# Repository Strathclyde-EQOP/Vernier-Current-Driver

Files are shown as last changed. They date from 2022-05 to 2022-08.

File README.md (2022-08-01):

# Vernier Current Driver

The Vernier Current Driver is an ultra low noise, programmable, bi-polar current source. It comes in two flavours:

1. Low Current Driver (LCD): designed to output current up to ~50 mA
2. High Current Driver (HCD): designed to output currents from ~50 mA to ~250 mA

## Releases

Checkout the [latest release](https://github.com/Strathclyde-EQOP/Vernier-Current-Driver/releases/latest) to download the latest verified version of the design. Releases include PDF schematics and gerber files, so there is no need to install/understand KiCAD in order to make a board.

Checkout the [dev branch](https://github.com/Strathclyde-EQOP/Vernier-Current-Driver/tree/dev) for the most up to date (but probably untested!) design.

## Performance

Three sample devices have been tested. For full details, see the companion paper or take a look a look in the [Testing](/Doc/Testing/) folder.

The headlines results:

|Configuration|CH1|CH2|CH3|
|---|---|---|---|
|LCD@10 mA<sub>MAX</sub> (10 ± 5 Hz average noise) | 151.1 pA√Hz | 147.4 pA√Hz | 146.3 pA√Hz |
|LCD@2.5 mA<sub>MAX</sub> (10 ± 5 Hz average noise) | 37.6 pA√Hz | 38.2 pA√Hz | 37.7 pA√Hz |
|HCD@250 mA<sub>MAX</sub> (10 ± 5 Hz average noise) | 4114.2 pA√Hz | 4125.3 pA√Hz | 4124.1 pA√Hz |
|LCD@10 mA<sub>MAX</sub> (10 ± 5 Hz relative average noise) | 15.05 ppb√Hz | 14.68 ppb√Hz | 14.57 ppb√Hz |
|LCD@2.5 mA<sub>MAX</sub> (10 ± 5 Hz relative average noise) | 15.06 ppb√Hz | 15.29 ppb√Hz | 15.10 ppb√Hz |
|HCD@250 mA<sub>MAX</sub> (10 ± 5 Hz relative average noise) | 16.46 ppb√Hz | 16.50 ppb√Hz | 16.50 ppb√Hz |

noise_spectra

## Manual

For more information checkout the [Getting Started Guide](Doc/README.md).

## Publication

If you're the academic type, lots more detail on the design and testing of the Vernier Current Source can be found in our open-access paper, available as a pre-print on [arXiv](https://arxiv.org/abs/2207.10348).

## Citing

When citing this work in an academic context, please cite the paper as you normally would.

Outside of academic work, please link directly to this GitHub repo.

Lastly, if you make one and you like it (or don't like it), we would love to know!

## License

This work is licensed under a [Creative Commons Attribution-ShareAlike 4.0 International License](https://creativecommons.org/licenses/by-sa/4.0/).

## Authors

This work was created by [Marcin Mrozowski](https://eqop.phys.strath.ac.uk/people/marcin-mrozowski/) and [Iain Chalmers](https://www.linkedin.com/in/iain-chalmers-0394753b)
from the [Experimental Quantum Optics and Photonics](http://photonics.phys.strath.ac.uk/)
group at the University of Strathclyde.

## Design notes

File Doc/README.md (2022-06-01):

# Getting Started

1. Decide which device you want to make. If the maximum current you need is <50 mA, use a Low Current Driver (LCD). For larger current, up to 250 mA, use a High Current Driver.
2. Decided the maximum output current and bandwith you need, and calculate the components you should use. See [Customising Vernier Current Sources](Customisation.md) for help.
3. If you make an HCD, don't forget to [bias the driving stage](HCD-Biasing.md).
4. Make an enclosure and get connected. See [Getting Connected](GettingConnected.md) for details.
5. Program the Arduino using [the sample firmware](/Software/CurrentDriverFirmware/README.md), or write your own. Don't forget to set the board-specific parameters that are stored in the EEPROM.
6. Use it in your application!

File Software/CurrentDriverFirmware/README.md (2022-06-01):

# Current Driver Firmware

This example Vernier Current Driver firmware is designed to run on an [Arduino Nano Every](), although a regular Nano is compatible in a pinch (with slightly reduced functionality). It can be used as the basis for writing your own custom firmware to drive the currents needed for specific applications.

# Libraries

This firmware makes use of the [Arduino-CommandParser library](https://github.com/Uberi/Arduino-CommandParser). You need to install the library before you can compile the firmware.

# Connection

Connect to the USB Serial interface using the application of your choice.

# Commands

All command packets are started with a `<` and end in a `>` character. The default serial is 1M-8-N-1.

Commands which query start with a `?`.

Commands which perform an action start with a `!`.

Respones to a command all start with a `#` and end with `\r\n`.

## Example

To set channel 1 to midrange (i.e. no current output), you would send the command `<!chan 1 32768>`.

### Command: `?`

**Description:**
Basic comms check.

**Arguments:**
None.

**Response:**
Always returns `#check`.

### Command: `?chan {channel_number}`

**Description:**
Get the current DAC code being output on {channel_number}. See the project wiki for details on how the DAC code and output current are related.

**Arguments:**
[0] - channel_number: Channel number to query, range 1 to 3.

**Response:**
Valid arguments result in a response in the form of `#{channel_number} {setpoint}`, confirming the set values.
Invalid arguments result in a reponse of `#ERROR`.

### Command: `!chan {channel_number} {setpoint}`

**Description:**
Set a channel to a specific DAC code. See the project wiki for details on how DAC code and output current are related.

**Arguments:**
[0] - channel_number: Channel number to update, range 1 to 3.
[1] - setpoint: DAC code to set channel to, range 0 to 65535.

**Response:**
Valid arguments result in a response in the form of `#{channel_number} {setpoint}`, confirming the set values.
Invalid arguments result in a reponse of `#ERROR`.

### Command: `!ramp {channel_number} {start} {step} {count}`

**Description:**
Setup a ramp output for a given channel. The start point is output immediately. Triggering the channel output (either with a !next command or via a trigger on a digital IO) will add {step} to the current output code. The output saturates after {count} triggers.

**Arguments:**
[0] - channel_number: Channel number to query, range 1 to 3.
[1] - start: The inital DAC count to output.
[2] - step: The number of DAC counts to increment by on a trigger.
[3] - count: The maximum number of triggers before the DAC output saturates.

**Response:**
Valid arguments result in a response in the form of `#{channel_number} {start} {step} {count}`, confirming the set values.
Invalid arguments result in a reponse of `#ERROR`.

### Command: `!next {channel_number}`

**Description:**
Triggers the given channel to move to the next output code.

**Arguments:**
[0] - channel_number: Channel number to query, range 1 to 3. Must be an integer.

**Response:**
Responds `#DONE` on success.
Responds `#ERROR {code}` on error. Error codes:

- -1: invalid channel.
- -2: channel not configured for stepping.

### Command: `?software`

**Description:**
Get the current software version string.

**Arguments:**
None.

**Response:**
The software version string in the form `#{version_string}`.

### Command: `?current`

**Description:**
Get the maximum output current in nanoamps.

**Arguments:**
None.

**Response:**
The maximum output current in the form `#{max_current} nA`.

### Command: `!current {max_current_nA}`

**Description:**
Set the maximum output current for the current driver in nanoamps.
The value is stored in EEPROM and persists between power cycles.

**Arguments:**
[0] - max_current_nA: The maximum output current in nA. Must be an integer.

**Response:**
Valid arguments result in a response in the form of `#{max_current_nA} nA`, confirming the set values.
Invalid arguments result in a reponse of `#ERROR`.

### Command: `?boardid`

**Description:**
Get the board ID.

**Arguments:**
None.

**Response:**
The board id string in the form `#{board_id}`.

### Command: `!boardid {id}`

**Description:**
Set the board ID.
The value is stored in EEPROM and persists between power cycles.

**Arguments:**
[0] - id: A string of up to 15 characters. Longer strings will be truncated.

**Response:**
The board id in the form `#{board_id}`.

### Command: `?hardware`

**Description:**
Get the hardware version.

**Arguments:**
None.

**Response:**
The hardware version string in the form `#{version_string}`.

### Command: `!hardware {version_string}`

**Description:**
Set the hardware version.
The value is stored in EEPROM and persists between power cycles.

**Arguments:**
[0] - version_string: A string of up to 15 characters. Longer strings will be truncated.

**Response:**
The hardware version in the form `#{version_string}`.

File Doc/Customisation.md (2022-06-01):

# Customising Vernier Current Drivers

To get the best noise performance, we recommend adapting the design to meet the requirements of specific applications. The two main specifications that can be adapted are the maximum output current and the output bandwidth.

# Setting The Maximum Output Current

The maximum output current for a Vernier Current Driver, $I_{max}$, should be configured to be as low as possible while still supplying the maximum current required. Doing so has two benefits:

1. The noise floor increases as $I_{max}$ increases (and is largely independent of what current the device is programmed to supply).
2. The current step size (i.e. the smallest programmable change in output current) increases with $I_{max}$.

## Configuring the LCD Maximum Output Current

The output of the LCD is based around a [Howland Current Pump](https://www.allaboutcircuits.com/technical-articles/the-howland-current-pump/) (HCP). Setting the output current on a channel requires changing 4 resistors. The excerpt below shows the HCP for Channel 1:

HCP

The current setting resistors are R38, R39, R44 and R45. The maximum output current is defined by the equation:

$$I_{max} = V_{REF} * \frac{1}{R_{f}}$$

where $R_{f} = R38 = R39 = R44 = R45$, and $V_{REF}$ is the reference voltage (2.5 V) from the LTC6655-2.5. As given in the schematic, $I_{max}=2.5\:mA$.

It is important that the resistor are of equal value, low tolerance (<= 0.1%) and low temperature coefficient (<= 25 ppm/°C). Changing the resistors will also require a change of the feedback capacitor (in this case C1) to maintain the previous bandwidth.

We have tested LCD devices configured for $I_{max}$ as low as 2.5 mA, and as high as 10 mA, but expect anything in the range of 25 μA to 50 mA to work.

## Configuring The HCD Maximum Output Current

Unlike the LCD, setting the maximum output current on the an HCD only requires changing one resistor per channel. The excerpt below shows the driving stage for Channel 1 on the HCD:

HCD

The current setting resistor is R48. The maximum output current is determined by the same equation as for the LCD:

$$I_{max} = V_{REF} * \frac{1}{R_{f}}$$

where $R_{f} = R48$, and $V_{REF}$ is the reference voltage (2.5 V) from the LTC6655-2.5. As given in the schematic, $I_{max}=192\:mA$.

If you change the feedback resistor on a board, don't forget to [re-adjust the transistor bias potentiometers](HCD-Biasing.md).

We have tested HCD devices with $I_{max}$ as high as 250 mA. For currents lower than 50 mA, it is better to use an LCD.

# Setting The Bandwidth

The output bandwidth of a Vernier Current Driver should be scaled to the intended application. For example in an application where the static field is set once and never changed, it would be advantageous to use a small bandwidth to reduce wideband noise. In an application that sweeps a static field, a wider bandwidth would be required.

The output bandwidth for all Vernier Current Drivers depends on the bandwidth of the inverting summer stage and the Sallen-Key filter stage. LCD devices also depend on the Howland Current Pump stage.

It is a good idea to set all filtering stages to the same cutoff frequency.

## Configuring the Inverting Summer Bandwidth

The inverting summer stage bandwidth is controlled by changing one capacitor. The excerpt below shows the inverting summer stage for Channel 1:

inverting_summer

To set the bandwidth, change the capacitor C34 based on the equation:

$$f_{-3db}=\frac{1}{2 \pi RC}$$

where $R=R29$ and $C=C34$. Note that R29 should **NOT** be adjusted to configure the bandwidth, as it would affect the summing circuit. In the example above, $f_c=159\:Hz$.

## Configuring the Sallen-Key Low Pass Filter Bandwidth

The bandwidth of the Sallen-Key low pass filter depends on two capacitors and two resistors. he excerpt below shows the Sallen-Key filtering stage for Channel 1:

sallen-key

The cutoff frequency for for the above low pass Sallen-Key filter is defined as:

$$f_{-3db}=\frac{1}{2 \pi R_{32} C_{52} R_{35} C_{49}}$$

It is recommended to leave the resistor values and only adapt the capacitor values to define the bandwidth.

## Configuring the Howland Current Pump Bandwidth (LCD Only)

Additional filtering is available on LCD devices by changing the feedback capacitor for the Howland Current Pump. The equation for the cuttoff frequency is:

$$f_{-3db}=\frac{1}{2 \pi RC}$$

where $R=R44$ and $C=C1$ in the excerpt in the [Configuring the LCD Maximum Output Current](#configuring-the-LCD-Maximum-Output-current) section.

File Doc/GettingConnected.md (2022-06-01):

# Getting Connected

## Enclosure

The Vernier Current Driver is designed to fit in a [Hammond 1455N1601](Doc/Customisation.md) enclosure. You can find our front/back panel machining template [here]().

Artboard 1

## Power

The coil driver is simple to operate. It requires a split rail power supply capable of supply ±11-16V: going beyond this range will trip the over-voltage protection. The device features a reverse polarity protection on it's power inputs.

## External Interface

The back panel features:

* **+V, GND, -V** - power inputs (accepts standard 4mm banana jacks).
* **ON/OFF switch** - this switch is a "soft" power switch which still supplies the power for the PG LEDs as well as low power indicator circuitry even when it is in "OFF" position. The standby current in this mode is less than 1 mA.
* **PG +V, PG -V LEDs** - power good LEDs that indicate input power has been applied in the correct polarity.
* **Battery low +V, -V** - low battery indicators. These LEDs will light up if the voltage falls below 11 V. Useful if you use lead-acid batteries to power the device.
* **PG +7.5V, +5V, -7.5V** - regulator power good indicators. These LEDs will light up if the PG flag has been raised for the ±7.5 V and 5 V rails.
* **Micro USB input** - USB interface for programming and control.

The front panel features:

* **Three output BNCs** - current output for each channel.
  * **_Note:_** BNCs on LCDs are _**referenced to ground**_ while HCD BNCs float via a resistor to ground. _**Do not**_ plug HCD output channels to any instrumentation that has a single-ended connection to ground!
* **RJ45 output** - an alternative output for the three channels. Pin arrangement CH1 (+ -) (7 8), CH2 (+ -) (4 5), CH3 (+ -) (1 2), GND (3 6). Useful for sending currents over inexpensive Cat5 twisted pairs.

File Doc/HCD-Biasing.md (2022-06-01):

# Biasing The Drive Transistors on HCDs

To ensure the HCD works as intended and does not go into thermal runaway, it is important to bias the driving transistors correctly using the onboard potentiometers. This can be achieved by using the potentiometers pair on each channel.

To correctly bias the transistors:

1. Power the HCD from a lab power supply with an adjustable current limit. Set the limit to 130% of $I_{max}$.
2. Set both potentiometers (RV1 and RV2) to 7 kΩ. You can check their resistance by probing TP55 and TP56 as well as TP57 and TP58 (or the equivalent on other channels).
3. Program the driver to supply maximum positive output current.
4. Connect the output to a current meter.
5. Adjust RV1 until you find the point where the current starts to drop from the maximum, then back off by half a turn (i.e. so that you are half a turn into the saturation region).
6. Program the driver to supply maximum negative output current and repeat for RV2.

Ideally, the device should be tested to ensure that no thermal-runaway condition is reached by changing the output current in the following order:

1. Max +ve current for 120 seconds
2. Zero current for 120 seconds
3. Max -ve current for 120 seconds.
4. Zero current for 120 seconds.

You can tell the device has gone into thermal runaway if, after returning to zero, the power draw from the supply does not drop. If the device goes into thermal runaway, the potentiometers need to be re-adjusted.

HCD

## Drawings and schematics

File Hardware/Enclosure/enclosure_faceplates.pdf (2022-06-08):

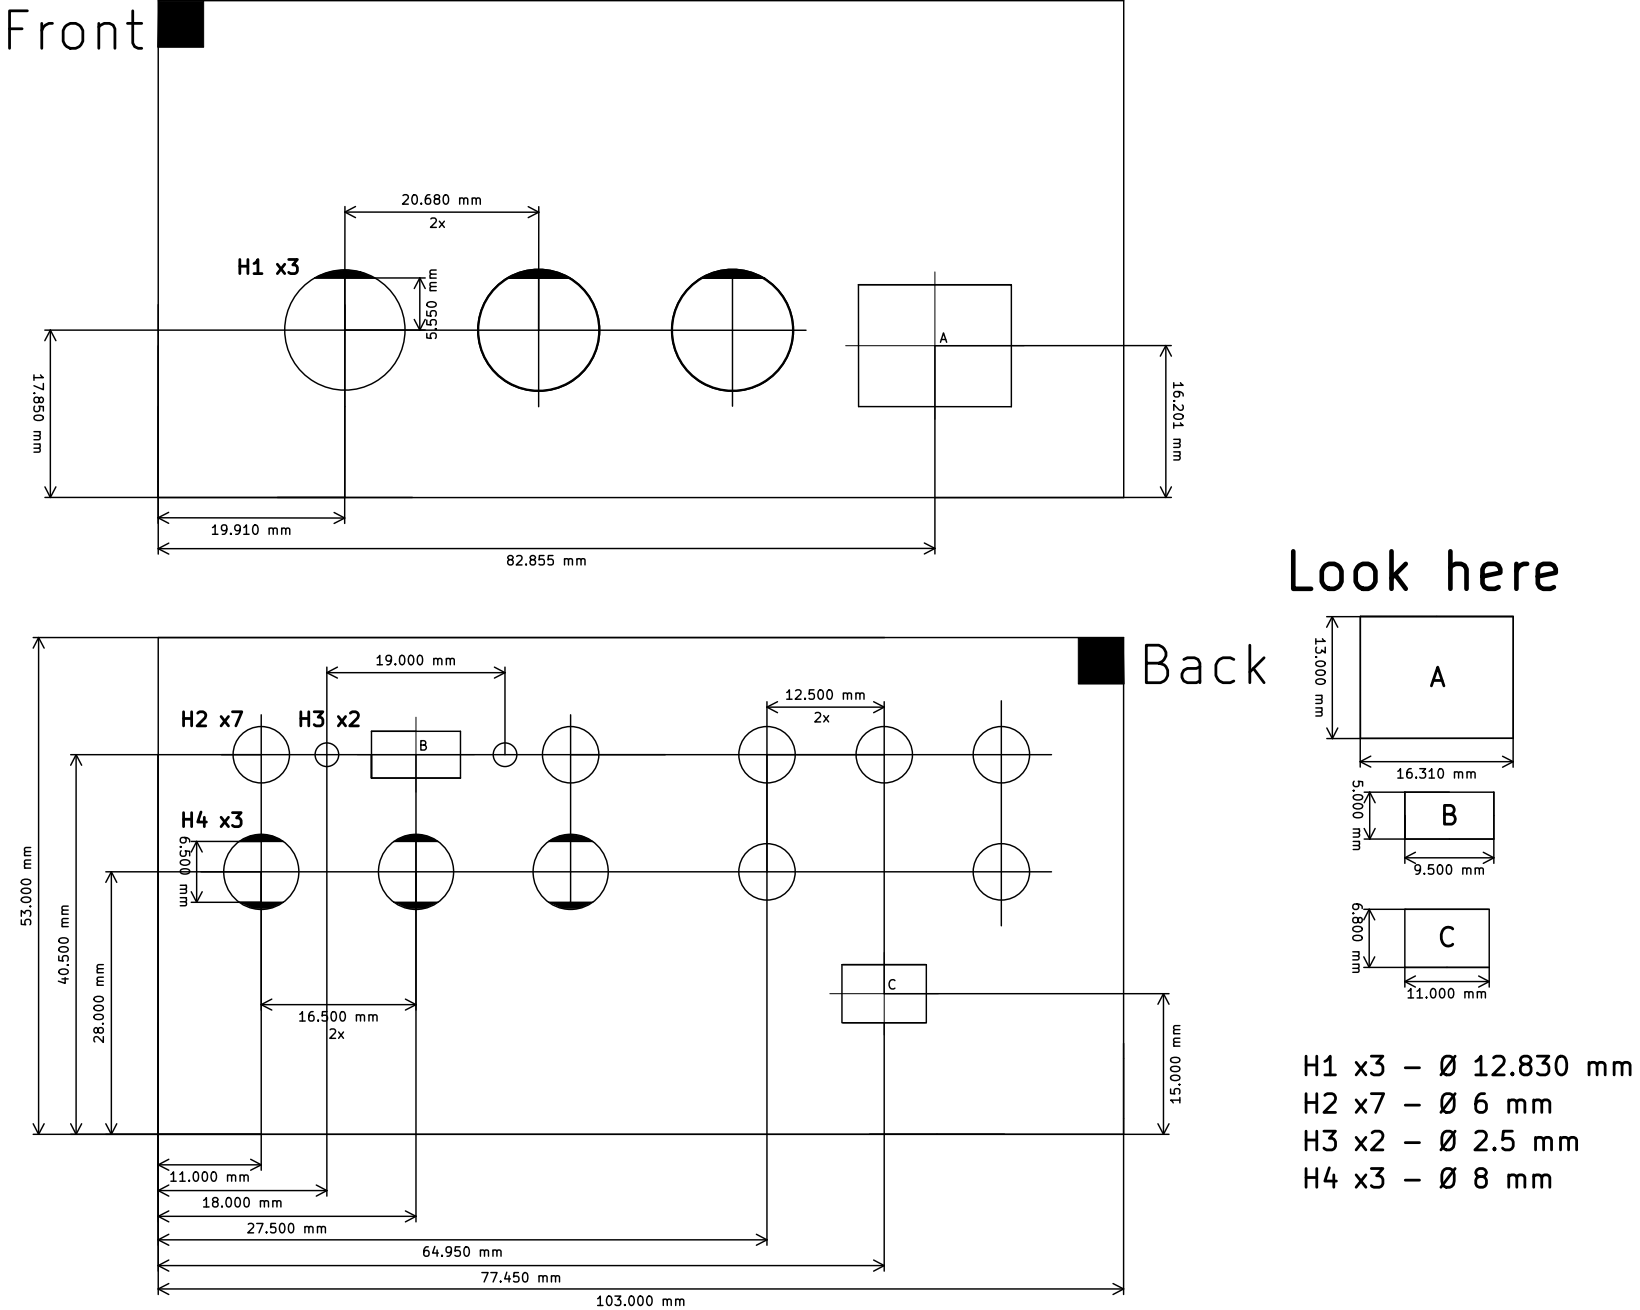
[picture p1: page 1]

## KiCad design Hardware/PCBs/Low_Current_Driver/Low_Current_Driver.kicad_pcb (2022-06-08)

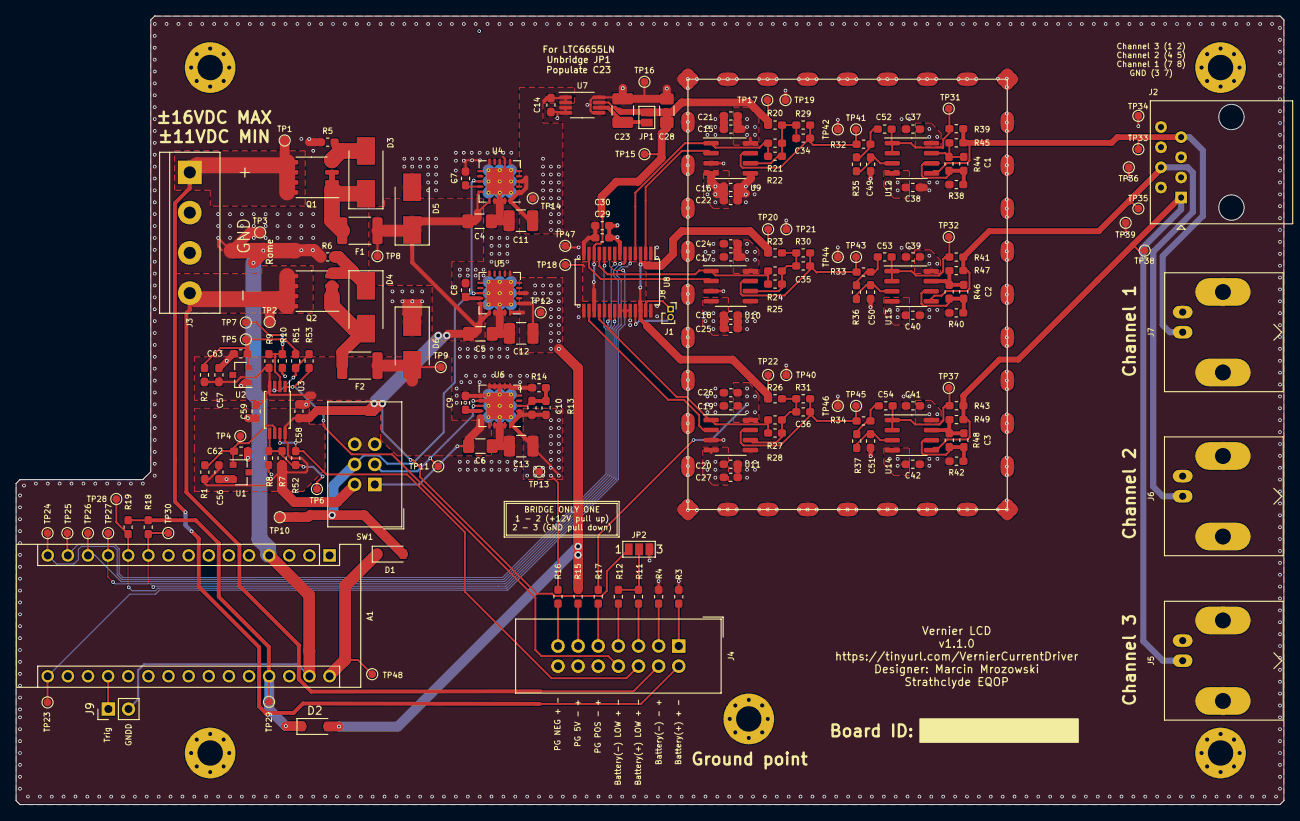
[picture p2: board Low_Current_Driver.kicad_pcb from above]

Board: 4 copper layers, 160.0 x 99.5 mm, 194 parts (0 on the bottom side), 78 nets.

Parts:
A1: Arduino_Nano_Every; Arduino_Nano
C1, C2, C3, C7, C8, C9, C21, C22, C24, C25, C26, C27, C49, C50, C51, C52, C53, C54: 1u; C_0603_1608Metric_Pad1.05x0.95mm_HandSolder
C4, C5, C6, C28: 10u; C_1206_3216Metric_Pad1.42x1.75mm_HandSolder
C10, C29: 10n; C_0603_1608Metric_Pad1.05x0.95mm_HandSolder
C11, C12, C13, C23: 47u; C_1210_3225Metric_Pad1.42x2.65mm_HandSolder
C14, C15, C16, C17, C18, C19, C20, C30, C34, C35, C36, C37, C38, C39, C40, C41, C42, C56, C57, C58, C59, C62, C63: 100n; C_0603_1608Metric_Pad1.05x0.95mm_HandSolder
D1, D2: MBR0520LT; D_SOD-123
D3, D4, D5, D6: SMBJ16A; D_SMB_Handsoldering
F1, F2: 1A; Fuse_1812_4532Metric_Pad1.30x3.40mm_HandSolder
H1, H2, H3, H4, H5: MountingHole_Pad; MountingHole_3.2mm_M3_Pad_Via
J1: Conn_01x02; PinSocket_1x02_P1.00mm_Vertical_CUSTOM_CYD
J2: RJ45; RJ45_Amphenol_54602-x08_Horizontal
J3: Screw_Terminal_01x04; TerminalBlock_bornier-4_P5.08mm
J4: Conn_02x07_Odd_Even; IDC-Header_2x07_P2.54mm_Vertical
J5: Channel 3; BNC_Amphenol_B6252HB-NPP3G-50_Horizontal
J6: Channel 2; BNC_Amphenol_B6252HB-NPP3G-50_Horizontal
J7: Channel 1; BNC_Amphenol_B6252HB-NPP3G-50_Horizontal
J8: MS548-10F; MS548-10C
J9: Conn_01x02; PinHeader_1x02_P2.54mm_Vertical
JP1: SolderJumper_2_Open; SolderJumper-2_P1.3mm_Open_Pad1.0x1.5mm
JP2: SolderJumper_3_Open; SolderJumper-3_P1.3mm_Open_Pad1.0x1.5mm_NumberLabels
NT1: Net-Tie_3; NetTie-3_SMD_Pad2.0mm
Q1: Si4447ADY; SO-8_3.9x4.9mm_P1.27mm
Q2: IRF8707PbF; SO-8_3.9x4.9mm_P1.27mm
R1, R2, R3, R4, R5, R6, R11, R12, R15, R16, R17, R18, R19, R20, R21, R22, R23, R24, R25, R26, R27, R28, R29, R30, R31: 10k; R_0603_1608Metric_Pad1.05x0.95mm_HandSolder
R7: 120k; R_0603_1608Metric_Pad1.05x0.95mm_HandSolder
R8, R10: 100k; R_0603_1608Metric_Pad1.05x0.95mm_HandSolder
R9, R53: 133k; R_0603_1608Metric_Pad1.05x0.95mm_HandSolder
R13: 549k; R_0603_1608Metric_Pad1.05x0.95mm_HandSolder
R14: 102k; R_0603_1608Metric_Pad1.05x0.95mm_HandSolder
R32, R33, R34, R35, R36, R37, R38, R39, R40, R41, R42, R43, R44, R45, R46, R47, R48, R49: 1k; R_0603_1608Metric_Pad1.05x0.95mm_HandSolder
R51: 3k; R_0603_1608Metric_Pad1.05x0.95mm_HandSolder
R52: 2M; R_0603_1608Metric_Pad1.05x0.95mm_HandSolder
SW1: DPDT_Hirose; IDC-Header_2x03_P2.54mm_Vertical
TP1, TP2, TP3, TP4, TP5, TP6, TP7, TP8, TP9, TP10, TP11, TP12, TP13, TP14, TP15, TP16, TP17, TP18, TP19, TP20, TP21, TP22, TP23, TP24, TP25, TP26, TP27, TP28, TP29, TP30, TP31, TP32, TP33, TP34, TP35, TP36, TP37, TP38, TP39, TP40, TP41, TP42, TP43, TP44, TP45, TP46, TP47, TP48: TestPoint_Probe; TestPoint_Pad_D1.0mm
U1, U2: LM4040DBZ-5; SOT-23
U3: LM393; TSSOP-8_4.4x3mm_P0.65mm
U4, U5: TPS7A470x; QFN-20-1EP_5x5mm_P0.65mm_EP3.35x3.35mm_ThermalVias
U6: TPS7A33; QFN-20-1EP_5x5mm_P0.65mm_EP3.35x3.35mm_ThermalVias
U7: LTC6655-2.5; MSOP-8_3x3mm_P0.65mm
U8: DAC8814; SSOP-28_5.3x10.2mm_P0.65mm
U9, U10, U11, U12, U13, U14: OPA2210; SOIC-8_3.9x4.9mm_P1.27mm

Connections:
+5V: C12.1, C29.1, C30.1, D2.2, R15.1, TP12.1, U5.1, U5.3, U5.20, U8.7
+5VD: A1.27, D2.1, R18.2, R19.2, TP29.1
+7V5: C11.1, C14.1, C15.1, C17.1, C19.1, C21.1, C24.1, C26.1, C37.1, C39.1, C41.1, R17.1, TP14.1, U4.1, U4.3, U4.20, U7.1, U7.2, U9.8, U10.8, U11.8, U12.8, U13.8, U14.8
+12V_batt_post: D1.2, SW1.4, TP10.1, U4.13, U5.13
+BATT: J3.1, J4.2, Q1.5, Q1.6, Q1.7, Q1.8, TP1.1
-7V5: C10.1, C13.1, C16.2, C18.2, C20.2, C22.2, C25.2, C27.2, C38.2, C40.2, C42.2, R13.1, R16.1, TP13.1, U6.1, U6.2, U6.20, U9.4, U10.4, U11.4, U12.4, U13.4, U14.4
-BATT: J3.4, J4.4, Q2.5, Q2.6, Q2.7, Q2.8, TP2.1
/Channel_Outputs/4Q_DAC_OUT_1: C34.2, R29.2, R32.2, TP41.1, U9.7
/Channel_Outputs/4Q_DAC_OUT_2: C35.2, R30.2, R33.2, TP43.1, U10.7
/Channel_Outputs/4Q_DAC_OUT_3: C36.2, R31.2, R34.2, TP45.1, U11.7
/Channel_Outputs/Coil_Iout_1: J2.7, J7.1, R39.1, R45.2, TP33.1, U12.5
/Channel_Outputs/Coil_Iout_2: J2.4, J6.1, R41.1, R47.2, TP35.1, U13.5
/Channel_Outputs/Coil_Iout_3: J2.1, J5.1, R43.1, R49.2, TP38.1, U14.5
/DAC/CLK: A1.16, TP23.1, U8.9
/DAC/Iout_D: J1.1, U8.27
/DAC/MSB: A1.11, R19.1, TP28.1, U8.5
/DAC/Rrb_D: J1.2, U8.25
/DAC/SDI: A1.14, TP25.1, U8.10
/DAC/SDO: A1.15, TP24.1, U8.20
/DAC/Vref_2.5V: C28.1, JP1.2, R20.1, R23.1, R26.1, TP15.1, TP17.1, TP18.1, TP20.1, TP22.1, U7.7, U8.3, U8.12, U8.17, U8.26
/DAC/~CS: A1.13, TP26.1, U8.8
/DAC/~LDAC: A1.12, TP27.1, U8.21
/DAC/~RS: A1.10, R18.1, TP30.1, U8.6
/MCU/Trigger: A1.19, J9.1
/Power/+12VDC_bat: C4.1, C5.1, C56.1, C58.1, D5.1, F1.1, JP2.1, R1.2, R7.1, SW1.2, TP8.1, U3.8, U4.15, U4.16, U5.15, U5.16
/Power/-12VDC_bat: C6.1, C57.1, C59.1, D6.2, F2.1, R2.2, R9.1, SW1.1, TP9.1, U3.4, U6.15, U6.16
/Power/-EN: SW1.3, TP11.1, U6.13
/Power/Battery_Management/+5V_c_ref: C62.1, R1.1, TP4.1, U1.1, U3.6
/Power/Battery_Management/+5_PG_A: J4.11, R15.2
/Power/Battery_Management/+7.5_PG_A: J4.9, R17.2
/Power/Battery_Management/-5V_c_ref: C63.1, R2.1, R51.2, TP5.1, U2.2
/Power/Battery_Management/-7.5_PG_C: J4.13, R16.2
/Power/Battery_Management/Battery+_C: J4.1, R3.1
/Power/Battery_Management/Battery+_LOW_A: J4.5, R11.2
/Power/Battery_Management/Battery+_LOW_C: J4.6, R52.1, U3.7
/Power/Battery_Management/Battery-_A: J4.3, R4.1
/Power/Battery_Management/Battery-_LOW_A: J4.7, R12.2
/Power/Battery_Management/Battery-_LOW_C: J4.8, R53.1, U3.1
GND: C4.2, C5.2, C6.2, C7.2, C8.2, C9.2, C11.2, C12.2, C13.2, C14.2, C15.2, C16.1, C17.2, C18.1, C19.2, C20.1, C21.2, C22.1, C23.2, C24.2, C25.1, C26.2, C27.1, C28.2, C29.2, C30.2, C37.2, C38.1, C39.2, C40.1, C41.2, C42.1, C49.2, C50.2, C51.2, C56.2, C57.2, C58.2, C59.2, C62.2, C63.2, D5.2, D6.1, H1.1, H2.1, H3.1, H4.1, H5.1, J2.2, J2.3, J2.5, J2.6, J2.8, J3.2, J3.3, J4.10, J4.12, J4.14, J5.2, J6.2, J7.2, J8.1, JP2.3, NT1.1, NT1.3, R3.2, R4.2, R5.2, R6.2, R8.2, R10.2, R14.2, R38.2, R40.2, R42.2, SW1.5, SW1.6, TP3.1, TP16.1, TP19.1, TP21.1, TP34.1, TP36.1, TP39.1, TP40.1, TP42.1, TP44.1, TP46.1, TP47.1, U1.2, U2.1, U4.6, U4.7, U4.8, U4.9, U4.10, U4.12, U4.17, U4.18, U4.19, U4.21, U5.6, U5.7, U5.10, U5.17, U5.18, U5.19, U5.21, U6.6, U6.7, U6.8, U6.9, U6.10, U6.11, U6.12, U6.17, U6.18, U6.19, U6.21, U7.3, U7.4, U7.5, U7.8, U8.1, U8.14, U8.15, U8.22, U8.23, U8.24, U8.28, U9.3, U9.5, U10.3, U10.5, U11.3, U11.5
GNDD: A1.4, A1.29, J9.2, NT1.2
unnamed: A1.30, D1.1, TP48.1
unnamed: C1.1, R44.1, R45.1, U12.7
unnamed: C1.2, R38.1, R44.2, U12.6
unnamed: C2.1, R46.1, R47.1, U13.7
unnamed: C2.2, R40.1, R46.2, U13.6
unnamed: C3.1, R48.1, R49.1, U14.7
unnamed: C3.2, R42.1, R48.2, U14.6
unnamed: C7.1, U4.14
unnamed: C8.1, U5.14
unnamed: C9.1, U6.14
unnamed: C10.2, R13.2, R14.1, U6.3
unnamed: C23.1, JP1.1, U7.6
unnamed: C34.1, R20.2, R21.2, R22.2, R29.1, U9.6
unnamed: C35.1, R23.2, R24.2, R25.2, R30.1, U10.6
unnamed: C36.1, R26.2, R27.2, R28.2, R31.1, U11.6
unnamed: C49.1, R35.1, U12.3
unnamed: C50.1, R36.1, U13.3
unnamed: C51.1, R37.1, U14.3
unnamed: C52.1, R39.2, TP31.1, U12.1, U12.2
unnamed: C52.2, R32.1, R35.2
unnamed: C53.1, R41.2, TP32.1, U13.1, U13.2
unnamed: C53.2, R33.1, R36.2
unnamed: C54.1, R43.2, TP37.1, U14.1, U14.2
unnamed: C54.2, R34.1, R37.2
unnamed: D3.1, F1.2, Q1.1, Q1.2, Q1.3
unnamed: D3.2, Q1.4, R5.1
unnamed: D4.1, Q2.4, R6.1
unnamed: D4.2, F2.2, Q2.1, Q2.2, Q2.3
unnamed: JP2.2, R11.1, R12.1
unnamed: R9.2, R10.1, TP7.1, U3.2
unnamed: R21.1, R22.1, U8.4, U9.1
unnamed: R24.1, R25.1, U8.11, U10.1
unnamed: R27.1, R28.1, U8.18, U11.1
unnamed: R51.1, R53.2, U3.3
unnamed: R7.2, R8.1, R52.2, TP6.1, U3.5
unnamed: U8.2, U9.2
unnamed: U8.13, U10.2
unnamed: U8.16, U11.2

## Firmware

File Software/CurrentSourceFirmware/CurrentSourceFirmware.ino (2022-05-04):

/* Control firmware for the EQOP Current Source.

  This software uses the CommandParser library, which needs to be
  installed for this code to compile. See the library GitHub for
  details:
    https://github.com/Uberi/Arduino-CommandParser

  Triggers: note that the Arduino Nano only supports external
  interrupts on D2 and D3. Therefore, by default a trigger on Channel
  3 is not supported. You can remap the channel trigger pin
  assignment as a workaround. The Nano Every supports external
  interrupts on every digital pin, and therefore is not limited to
  two trigger inputs.

  Copyright University of Strathclyde, 2022
*/


/*******************************************************************
  Includes
*******************************************************************/
#include <CommandParser.h>
#include <string.h>

#include "CurrentSource.h"
#include "HardwareInfo.h"


/*******************************************************************
  Configuration
*******************************************************************/
const char software_version[] = "1.0.2";
const uint32_t kBaudrate = 1000000;
HardwareSerial &SerialInUse = Serial;


/*******************************************************************
  Pin Mapping
*******************************************************************/
const uint8_t kPinCS = 10;
const uint8_t kPinLDAC = 9;
const uint8_t kPinMSB = 8;
const uint8_t kPinReset = 7;
const uint8_t kPinChan1Trigger = 2;
const uint8_t kPinChan2Trigger = 3;
const uint8_t kPinChan3Trigger = 4;


/*******************************************************************
  Global Variables
*******************************************************************/
const uint8_t kSerialRxBufferLength = 32;
char serial_rx_buffer[kSerialRxBufferLength];
CurrentSource current_source(kPinCS, kPinLDAC, kPinReset, kPinMSB);
HardwareInfo hardware_info(0);
typedef CommandParser<> MyCommandParser;
MyCommandParser command_parser;


/*******************************************************************
  Arduino Setup
*******************************************************************/
void setup()
{
  SerialInUse.begin(kBaudrate);
  InitTriggers();
  RegisterCommands();
  current_source.Begin();
}


/*******************************************************************
  Arduino Superloop
*******************************************************************/
void loop() {

  if (ReceivePacket()) {
    if (serial_rx_buffer[0] == '0' ||
        serial_rx_buffer[0] == '1' ||
        serial_rx_buffer[0] == '2') {
      ProcessLegacyCommand();
    }
    else {
      char response[MyCommandParser::MAX_RESPONSE_SIZE];
      command_parser.processCommand(serial_rx_buffer, response);
      SerialInUse.println(response);
    }
  }
}


/*******************************************************************
  Functions
*******************************************************************/

void RegisterCommands() {
  command_parser.registerCommand("?", "", &CmdCommsCheck);
  command_parser.registerCommand("!chan", "uu", &CmdSetChan);
  command_parser.registerCommand("?chan", "u", &CmdGetChan);
  command_parser.registerCommand("!ramp", "uuiu", &CmdSetRamp);
  command_parser.registerCommand("!next", "u", &CmdChannelNext);
  command_parser.registerCommand("?software", "", &CmdGetSoftwareVersion);
  command_parser.registerCommand("!current", "u", &CmdSetMaxCurrent);
  command_parser.registerCommand("?current", "", &CmdGetMaxCurrent);
  command_parser.registerCommand("!boardid", "s", &CmdSetBoardId);
  command_parser.registerCommand("?boardid", "", &CmdGetBoardId);
  command_parser.registerCommand("!hardware", "s", &CmdSetHardwareVersion);
  command_parser.registerCommand("?hardware", "", &CmdGetHardwareVersion);
}


void InitTriggers() {
  pinMode(kPinChan1Trigger, INPUT_PULLUP);
  attachInterrupt(digitalPinToInterrupt(kPinChan1Trigger), IntTriggerChan1, FALLING);

  pinMode(kPinChan2Trigger, INPUT_PULLUP);
  attachInterrupt(digitalPinToInterrupt(kPinChan2Trigger), IntTriggerChan2, FALLING);

  pinMode(kPinChan3Trigger, INPUT_PULLUP);
  attachInterrupt(digitalPinToInterrupt(kPinChan3Trigger), IntTriggerChan3, FALLING);
}


void IntTriggerChan1() {
  current_source.Next(1);
}


void IntTriggerChan2() {
  current_source.Next(2);
}


void IntTriggerChan3() {
  current_source.Next(3);
}


/*
  Receive packets on the serial interface. Should be called in the superloop to
  check for any new serial packets.

  Valid packets are any that fit in the receive buffer, as well as use a '<' to mark
  the start of a packet and a '>' to mark the end.

  The received packed is stored in the global serial_rx_buffer, stripped of the
  start/stop characters.

  Returns true when there is a new packet to be processed in the superloop.
*/
bool ReceivePacket()
{
  static boolean rx_in_prgress = false;  // Characters in the pipeline
  static byte rx_buffer_index = 0;
  char start_marker = '<';
  char end_marker = '>';
  char rx_character;

  while (SerialInUse.available() > 0) {
    rx_character = SerialInUse.read();
    if (rx_in_prgress == true) {
      if (rx_character != end_marker) {
        serial_rx_buffer[rx_buffer_index] = rx_character;
        rx_buffer_index++;
        if (rx_buffer_index >= kSerialRxBufferLength) {
          // The input buffer has overflowed, which can only be an invalid command.
          // Silently drop the buffer, and wait for a new start character.
          rx_in_prgress = false;
        }
      }
      else {
        serial_rx_buffer[rx_buffer_index] = '\0'; // terminate the string
        rx_in_prgress = false;
        return true;
      }
    }
    else {
      if (rx_character == start_marker) {
        rx_in_prgress = true;
        rx_buffer_index = 0;
      }
    }
  }

  return false;
}


/*
  Command: '?'

  Description:
    Basic comms check.

  Arguments:
    None.

  Response:
    Always returns '#check'.
*/
void CmdCommsCheck(MyCommandParser::Argument *args, char *response) {
  strlcpy(response, "#check", MyCommandParser::MAX_RESPONSE_SIZE);
}



/*
  Command: '!chan {channel_number} {setpoint}'

  Description:
    Set a channel to a specific DAC code. See the project wiki for details on how
    DAC code and output current are related.

  Arguments:
    [0] - channel_number: Channel number to update, range 1 to 3.
    [1] - setpoint: DAC code to set channel to, range 0 to 65535.

  Response:
     Valid arguments result in a response in the form of '#{channel_number} {setpoint}',
     confirming the set values.
     Invalid arguments result in a reponse of '#ERROR'.
*/
void CmdSetChan(MyCommandParser::Argument *args, char *response) {
  uint8_t channel = (uint8_t)args[0].asUInt64;
  uint16_t setpoint = (uint16_t)args[1].asUInt64;
  int res;

  res = current_source.SetChannelSetpoint(channel, setpoint);
  if (!res) {
    snprintf(response, MyCommandParser::MAX_RESPONSE_SIZE, "#%u %u", channel, setpoint);
  }
  else {
    strlcpy(response, "#ERROR", MyCommandParser::MAX_RESPONSE_SIZE);
  }
}


/*
  Command: '?chan {channel_number}'

  Description:
    Get the current DAC code being output on {channel_number}. See the project
    wiki for details on how the DAC code and output current are related.

  Arguments:
    [0] - channel_number: Channel number to query, range 1 to 3.

  Response:
     Valid arguments result in a response in the form of '#{channel_number} {setpoint}',
     confirming the set values.
     Invalid arguments result in a reponse of '#ERROR'.
*/
void CmdGetChan(MyCommandParser::Argument *args, char *response) {
  uint8_t channel = (uint8_t)args[0].asUInt64;
  uint16_t setpoint;

  if (current_source.ValidateChannel(channel)) {
    setpoint = current_source.GetChannelSetpoint(channel);
    snprintf(response, MyCommandParser::MAX_RESPONSE_SIZE, "#%u %u", channel, setpoint);
  }
  else {
    strlcpy(response, "#ERROR", MyCommandParser::MAX_RESPONSE_SIZE);
  }
}


/*
  Command: '!ramp {channel_number} {start} {step} {count}'

  Description:
    Setup a ramp output for a given channel. The start point is output immediately.
    Triggering the channel output (either with a !next command or via a trigger on a
    digital IO) will add {step} to the current output code. The output saturates
    after {count} triggers.

  Arguments:
    [0] - channel_number: Channel number to query, range 1 to 3.
    [1] - start: The inital DAC count to output.
    [2] - step: The number of DAC counts to increment by on a trigger.
    [3] - count: The maximum number of triggers before the DAC output saturates.

  Response:
     Valid arguments result in a response in the form of '#{channel_number} {start} {step} {count}',
     confirming the set values.
     Invalid arguments result in a reponse of '#ERROR'.
*/
void CmdSetRamp(MyCommandParser::Argument *args, char *response) {
  uint8_t channel = (uint8_t)args[0].asUInt64;
  uint16_t ramp_start = (uint16_t)args[1].asUInt64;
  int32_t ramp_step = (int32_t)args[2].asInt64;
  uint16_t ramp_count = (uint16_t)args[3].asUInt64;

  if (current_source.ValidateChannel(channel)) {
    current_source.InitRamp(channel, ramp_start, ramp_step, ramp_count);
    /* For some reason, a 4-parameter snprintf is always returning a 0 for the 4th parameter.
        Workaround is to just print directly to serial port for now, rather than copy into
        the response.
    */
    //    snprintf(
    //      response,
    //      MyCommandParser::MAX_RESPONSE_SIZE,
    //      "#%u %u %i %u",
    //      channel,
    //      ramp_start,
    //      ramp_step,
    //      ramp_count);
    SerialInUse.print('#');
    SerialInUse.print(channel);
    SerialInUse.print(' ');
    SerialInUse.print(ramp_start);
    SerialInUse.print(' ');
    SerialInUse.print(ramp_step);
    SerialInUse.print(' ');
    SerialInUse.print(ramp_count);
  }
  else {
    strlcpy(response, "#ERROR", MyCommandParser::MAX_RESPONSE_SIZE);
  }
}


/*
  Command: '!next {channel_number}'

  Description:
    Triggers the given channel to move to the next output code.

  Arguments:
    [0] - channel_number: Channel number to query, range 1 to 3. Must be an integer.

  Response:
     Valid arguments result in a response in the form of '#{channel_number} {start} {step} {count}',
     confirming the set values.
     Invalid arguments result in a reponse of '#ERROR'.
*/
void CmdChannelNext(MyCommandParser::Argument *args, char *response) {
  uint8_t channel = (uint8_t)args[0].asUInt64;
  current_source.Next(channel);
}


/*
  Command: '?software'

  Description:
    Get the current software version string.

  Arguments:
    None.

  Response:
     The software version string in the form '#{version_string}'.
*/
void CmdGetSoftwareVersion(MyCommandParser::Argument *args, char *response) {
  snprintf(response, MyCommandParser::MAX_RESPONSE_SIZE, "#%s", software_version);
}


/*
  Command: '?current'

  Description:
    Get the maximum output current in nanoamps.

  Arguments:
    None.

  Response:
     The maximum output current in the form '#{max_current} nA'.
*/
void CmdGetMaxCurrent(MyCommandParser::Argument *args, char *response) {
  snprintf(response, MyCommandParser::MAX_RESPONSE_SIZE, "#%ld nA", hardware_info.GetMaxCurrent());
}
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

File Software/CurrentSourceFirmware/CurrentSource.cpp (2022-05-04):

#include <avr/pgmspace.h>

#include "CurrentSource.h"
#include "calibration.h"


void CurrentSource::Begin() {
  digitalWrite(pin_cs, HIGH);
  pinMode(pin_cs, OUTPUT);

  digitalWrite(pin_ldac, LOW); //Disable LDAC - transparent DAC registers
  pinMode(pin_ldac, OUTPUT);

  digitalWrite(pin_reset, HIGH);
  pinMode(pin_reset, OUTPUT);

  digitalWrite(pin_msb, HIGH); //Hardware reset should output midrange
  pinMode(pin_msb, OUTPUT);

  SPI.begin();
  SPI.beginTransaction (SPISettings (2000000, MSBFIRST, SPI_MODE0));

  Reset();
}


void CurrentSource::Reset() {
  digitalWrite(pin_reset, LOW);
  delayMicroseconds(100);
  digitalWrite(pin_reset, HIGH);
  SetAllChannels(kResetSetpoint); // set all DAC to default setpoint
}


int8_t CurrentSource::SetChannelSetpoint(uint8_t channel, uint16_t code) {
  Channel *chan = GetChannel(channel);
  if (!chan) {
    return -1;
  }
  uint16_t calibrated_code = GetCalibratedCode(channel, code);
  WriteDAC(chan->dac_channel, calibrated_code);
  // Calibration is transparent to the user, so store the user
  // requested code and not the calibrated version.
  chan->setpoint = code;
  chan->state = Channel::State::STATIC;
  return 0;
}


uint16_t CurrentSource::GetChannelSetpoint(uint8_t channel) {
  Channel *chan = GetChannel(channel);
  if (!chan) {
    return 0;
  }
  return chan->setpoint;
}


int8_t CurrentSource::SetAllChannels(uint16_t code) {
  int8_t error = 0;

  for (uint8_t i = 0; i < kNumChannels; i++) {
    error += SetChannelSetpoint(channels[i].address, code);
  }
  return error;
}


uint16_t CurrentSource::GetCalibratedCode(uint8_t channel, uint16_t code) {
  Channel *chan = GetChannel(channel);
  if (!chan) {
    return 0;
  }
  uint16_t calibration_idx = code / kCalibrationStepSize;
  long temp_code = (long)code;
  long correction = (long)pgm_read_byte(&chan->calibration_table[calibration_idx]);

  temp_code = temp_code + correction;
  if (temp_code < 0) {
    temp_code = 0;
  }
  if (temp_code > 65535) {
    temp_code = 65535;
  }
  return (uint16_t)temp_code;
}


bool CurrentSource::ValidateChannel(uint8_t channel) {
  return GetChannel(channel) ? true : false;
}


void CurrentSource::WriteDAC(uint8_t address, uint16_t code) {
  digitalWrite(pin_cs, LOW);
  SPI.transfer(address);
  SPI.transfer(highByte(code));
  SPI.transfer(lowByte(code));
  digitalWrite(SS, HIGH);
}


Channel* CurrentSource::GetChannel(uint8_t channel) {
  for ( int i = 0; i < kNumChannels; i++) {
    if (channel == channels[i].address) {
      return &channels[i];
    }
  }
  return NULL;
}


int CurrentSource::InitRamp(uint8_t channel, uint16_t start, uint16_t step, uint16_t count) {
  Channel *chan = GetChannel(channel);
  if (!chan) {
    return -1;
  }
  chan->ramp.Begin(start, step, count);
  WriteDAC(chan->dac_channel, start);
  chan->setpoint = start;
  chan->state = Channel::State::RAMP;
  return 0;
}


void CurrentSource::Next(uint8_t channel) {
  Channel *chan = GetChannel(channel);
  if (!chan) {
    return;
  }
  if (chan->state != Channel::State::RAMP) {
    return;
  }
  uint16_t code = chan->ramp.Next();
  WriteDAC(chan->dac_channel, code);
  chan->setpoint = code;
}


void Ramp::Begin(uint16_t start, uint16_t step, uint16_t count) {
  this->start = start;
  this->step = step;
  this->count = count;
  current = start;
}


uint16_t Ramp::Next() {
  if (count > 0) {
    current += step;
    count--;
  }
  return current;
}

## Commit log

2020-03-13 Add files via upload
    Changed standard 2.54 mm connectors to Hirose DF11 series which are keyed.
    Revised some copper islands and optimised connections and labeling
    Added an interactive BOM to help with assembly
    [Channel_Outputs.sch, DAC.sch, MCU.sch, Power.sch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]
2020-03-16 2 mA coil driver WiP
    Update on work in progress 2 mA coil driver
    [Channel_Outputs.sch, DAC.sch, MCU.sch, Power.sch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]
2020-03-17 2 mA version changes
    2 mA version layout had been finalised
    -Board had been shortened to improve signal integrity
    -Power routing optimised
    -Minor fixes
    [Vernier_Vamp-2mA.kicad_pcb]
2020-04-27 Coil driver version 1.0B
    Updated coil driver 200mA version with fixes requested by Iain.
    [BMS.sch, Battery_Management.sch, Channel_Outputs.sch, DAC.sch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]
2020-04-30 Schematic and layout changes
    Schematic updates:
    - Added extra comments
    - Added description (BNC channels)
    - Moved mounting holes to the title block
    - Added an option for connecting low battery indicatior LEDs to either +12V or GND (Comparator pulls to -12V)
    - Added a 0R resistor for connecting +12V to Vin of nano
    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
    [Battery_Management.sch, DAC.sch, MCU.sch, Mounting_Holes.sch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]
2020-04-30 Silkscreen change
    Changed the date code to month/year format.
    [Vernier_Vamp-200mA.kicad_pcb]
2020-05-04 OPA1622 Power Pad Tented Vias
    -Created a footprint for OPA1622 that features tented vias on the power pad
    -Applied it to the schematic as well as layout
    [Channel_Outputs.sch]
2020-05-05 1.0B fixes for 2mA (schematic)
    Added 1.0B fixes to the 2mA version related to schematic cleanup, and addition of hysteresis and alternative way to power nano.
    [Battery_Management.sch, Channel_Outputs.sch, DAC.sch, MCU.sch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]
2020-05-12 200mA changes
    -Changed OPA1622 footprint to accommodate tented vias
    -Rounded edges of the board to reduce mechanical stress
    -Refined drawing dimensions
    -Added title block to every schematic and layout sheet.
    [Vernier_Vamp-200mA.kicad_pcb]
2020-05-12 Applied 1.0B changes to 2mA version
    [Battery_Management.sch, Channel_Outputs.sch, DAC.sch, MCU.sch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]
2020-05-18 Update DAC8814_Driver.ino
    -Restored previously added comments.
    -Added reset on pin 7 and set it up
2020-05-18 Cleaned redundant project files
    KiCad automatically creates project file when individual schematic sheet is opened.
    [Vernier_Vamp-2mA_Test.kicad_pcb]
2020-05-19 200mA via fix
    -Fixed incorrect assignment of vias
    -Re-worked the copper pours
    -Updated plotter settings for 200mA and 2mA version
    [Vernier_Vamp-200mA.kicad_pcb, Vernier_Vamp-2mA.kicad_pcb]
2020-07-13 HCP output fix
    Fixed the HCP output.
    [Channel_Outputs.sch]
2020-07-13 SPI fix
    Rewired the SDI and SDO so that they match the host pinout.
    [DAC.sch, MCU.sch]
2020-07-13 Fixed LDO programmable output
    Fixed the LDO so that the output matches with programmed one.
    [Power.sch]
2020-11-06 1.0C Initial commit
    -Fixed amplifier output
    -Changed connectors to IDC
    -Via perimeter added
    TODO:
    Add shielding over analogue section
    [Battery_Management.sch, Channel_Outputs.sch, MCU.sch, Power.sch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]
2020-11-09 PCB Update
    [Vernier_Vamp-2mA.kicad_pcb]
2020-11-11 Issue fixes
    This commit, addresses following issues:
    -Stray current at the output with only USB plugged in
    -RFI Shield over analogue circuitry
    -Wrong BNC connector footprint
    Some general layout optimisation
    [MCU.sch, Vernier_Vamp-2mA.kicad_pcb, Vernier_Vamp-2mA.sch]
2020-11-12 Silkscreen fixes
    Silkscreen settings changed so that references are not obstructed by the shield.
    -Added magnetic field direction designation for each channel.
    [Vernier_Vamp-2mA.kicad_pcb, Vernier_Vamp-2mA.sch]
2020-11-27 Change of J1 connector courtyard
    PCB footprint change:
    -J1 (1 mm pinheader) courtyard had been changed to pass DRC
    [MCU.sch, Vernier_Vamp-2mA.kicad_pcb, Vernier_Vamp-2mA.sch]
2021-05-12 2 mA changes
    -2 mA version is now called "low current coil driver" LCCD
    - Small changes to the PCB layout
    - Shield footprint correction
    - General optimisation
    [Power.sch, Vernier_Vamp-200mA.sch, Vernier_Vamp-2mA.kicad_pcb]
2021-05-18 1.0D Update
    LCCD changes
    -Addition of trigger for calibration
    -PCB optimisation
    HCCD changes
    -New output stage designed
    -Changes from 1.0C applied to HCCD
    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
    [Battery_Management.sch, Channel_Outputs.sch, DAC.sch, MCU.sch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]
2021-05-19 Silkscreen cleanup
    -Silkscreen cleanup
    -Unconnected items removed
    -Addition of calibration software
    -Addition of test points for shunt resistor on the bottom layer
    [Vernier_Vamp-200mA.kicad_pcb]
2021-05-19 Addition of test points onto the bias circuitry
    -Addition of test points onto the bias circuitry (HCCD)
    -Silkscreen update (LCCD)
    [Channel_Outputs.sch, Vernier_Vamp-200mA.kicad_pcb, Vernier_Vamp-2mA.kicad_pcb]
2022-03-29 Remove unused pin definitions
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2022-03-29 Replace calibration routine
    Previously, the array-per-channel meant needing to switch on the channel. Just making this a 2D array makes the code much cleaner.
2022-03-29 Remove unused calibration correction
    Existing code wasn't even using the calibration routine...
2022-03-29 Add calibration corrections
    The original calibration arrays were not being used, and were being optimised out. Once used, they were exceeding the RAM available on the Nano. Instead, moved the calibration corrections to PROGMEM.
    Calibrations are now automatically handled by the driver on calling set_dac().
2022-03-30 Fix stored setpoint
    Originally was storing the calibrated code sent to the DAC, but calibration should be transparent to the user. As such, store the code the user requested.
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2022-04-04 Fix calibration tables
    The old 2D correction table assumed channel number matched calibration table array index.
    Instead, store a pointer to the cirrection table for each channel so that the channel number is independent.
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2022-05-04 Delete Evaluation/OPA1622_eval directory
    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
    [OPA1622_eval.kicad_pcb, OPA1622_eval.sch]
2022-05-04 Change of name to Low Current Driver (LCD) filename
    [Battery_Management.sch, Channel_Outputs.sch, DAC.sch, Low_Current_Driver.kicad_pcb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]
2022-05-04 Change of name to Low Current Driver (LCD) folder
    [Battery_Management.sch, Channel_Outputs.sch, DAC.sch, Low_Current_Driver.kicad_pcb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]
2022-05-04 Change of name to High Current Driver (HCD) folder
    [BMS.sch, Battery_Management.sch, Channel_Outputs.sch, DAC.sch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]
2022-05-04 Change of name to High Current Driver (HCD) filename
    [Battery_Management.sch, Channel_Outputs.sch, DAC.sch, High_Current_Driver.kicad_pcb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]
2022-05-05 Silkscreen update HCD
    Removed EQOP specific "X" "Y" "Z" from the channels
    [High_Current_Driver.kicad_pcb]
2022-05-05 Silkscreen update LCD
    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
    [Low_Current_Driver.kicad_pcb]
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2022-06-06 HCD amplifier update
    - Updated OPA2277 amplifiers to OPA2210 that were actually populated on the boards.
    [Channel_Outputs.sch, DAC.sch, High_Current_Driver.kicad_pcb]
2022-06-06 LCD amplifier update
    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
    [MCU.sch]
2022-06-06 Collection of minor fixes
    - Added DNP to one of the power mux diodes
    - Added missing power flag
    [MCU.sch]
2022-06-06 Fill zones on LCD PCB
    [Low_Current_Driver.kicad_pcb]
2022-06-06 Update PCB from schematic
    There were no functional changes made. The netlist names were just slightly mismatched between the schematic and the PCB. Most the the difference from this commit are just line orderings seem to have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
    [High_Current_Driver.kicad_pcb]
2022-06-07 Move PCBs to subdirectory
    [BMS.sch, Battery_Management.sch, Channel_Outputs.sch, DAC.sch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]
2022-06-07 Switch to common footprint library
    [Channel_Outputs.sch, High_Current_Driver.kicad_pcb, High_Current_Driver.sch, Low_Current_Driver.kicad_pcb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]
2022-06-07 Switch to common shared library
    [Battery_Management.sch, Channel_Outputs.sch, DAC.sch, MCU.sch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]
2022-06-07 Replace OPA2270 with OPA2210
    These parts must have been missed somehow in 2617594b43217be702f357aa0c3cac4a60710900 and f9a9295af51ef93e9ca1b36aeebbcecdbb861685
    [DAC.sch]
2022-06-07 Place grid and drill/place origin at common location
    Just bottom left corner of the PCB.
    [High_Current_Driver.kicad_pcb, Low_Current_Driver.kicad_pcb]
2022-06-07 Update footprint to fix courtyard DRC error
    [High_Current_Driver.kicad_pcb, Low_Current_Driver.kicad_pcb]
2022-06-07 Fix malformed courtyard
    [High_Current_Driver.kicad_pcb]
2022-06-07 Bump version to 1.1.0
    [Battery_Management.sch, Channel_Outputs.sch, DAC.sch, High_Current_Driver.kicad_pcb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]
2022-06-07 Add repo link to silkscreen
    [High_Current_Driver.kicad_pcb, Low_Current_Driver.kicad_pcb]
